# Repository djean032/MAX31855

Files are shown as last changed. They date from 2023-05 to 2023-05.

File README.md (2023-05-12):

# MAX31855

## Project Description
A solution to control and monitor four thermocouples using the MAX31855 Thermocouple Amplifier.

## Contents
- Arduino Sketch
- Custom MAX31855 Library
- KICAD Generated Schematic and PCB
- Test Data

## Arduino Sketch

The Arduino sketch is designed to print both to a serial monitor on a PC and a LCD screen that is mounted on the device.

## MAX31855 Library

Custom library that creates a class instance of each thermocouple amplifier and provides functions to read data, check errors, and do a rational polynomial caluclation to accurately determine the temperature. Additionally a weighted average is used to filter the signal, resulting in a significantly smoothed reading.

The initial form of this library uses a switch statement to select the proper conversion function based on thermocouple type, of which only type 'T' and 'K' are currently supported. Additional types will be added in the future, so this library can be universally used across all thermocouple and MAX31855 types.

## Schematic


## Circuit Features

#### Overview

The circuit consists of four MAX31855 thermocouple amplifiers that are connected to an Arduino Micro. The Arduino Micro is connected to the the thermocouple amplifiers via SPI, utilizing the SCK, MISO, and CS lines. The Arduino also communicates the data to a PC via serial while also displaying it on an onboard LCD.

#### MAX31855 Idiosyncrasies

The MAX31855 transmits a cold-junction compensated thermocouple temperature, a cold-junction temperature (from a thermistor), and several fault checks over 32 bits. The first 14 bits are the cold-junction compensated thermocouple temperature, the next 12 bits are the cold-junction temperature, and the rest of the bits are either reserved bits or denote various fault checks.

The MAX31855 uses a linear conversion to convert the thermocouple voltage to a temperature. Specifically the type 'T' version uses a factor of $52.18 \frac{\mu V}{\textdegree C}$, which shows significant deviations at room temperature from tabulated values. For this application, this is not a suitable conversion method, so a rational polynomial function was employed in software to more accurately  model the thermocouple response. The basic steps are to convert the measured thermocouple temperature to a voltage using the linear relationship stated in the datasheet. Then a switch statement is used to slect the type of chip to determine the appropriate coefficients for the rational polynomial function. Finally, the thermocouple voltage and coefficients are used in the rational polynomial function to compute a corrected temperature. This was tested at several temperatures and provides an acceptable level of accuracy.

#### Data Transfer

The data is simultaneously displayed on an LCD screen and transmitted to a PC via USB, where it is read into our lab's LabView program used to control our spectrometer. The data is "filtered" using a weighted average that takes a weighted average of the previous value with the current value. This weight can be adjusted via software. 30% of the previous value seems to be a sweet spot between data smoothing and quick response time.

#### Power Supply

The device is powered via a 9V external AC to DC power supply. In our current application, we have an approximately 15m USB cable, which is triple the specification for USB 2.0. 

#### Miscellaneous

The MAX31855 requires 3.3V to operate, while the Arduino Micro operates at 5V, so two bi-directional level shifters were used for the data and power lines for the thermocouple amplifiers.

## PCB


## Evaluation

#### Summary
Overall, once the rational polynomial function and filtering was added, the performance was adequate for our lab's needs. It successfully reads temperatures from boiling water down to cryogenic temperatures used in our lab's spectrometer.

#### Data
|        Cooling Bath         | Measured Temperature ($\degree C$) | Theoretical Value ($\degree C$) |
|:---------------------------:|:----------------------------------:|:-------------------------------:|
|          Ice Water          |                -2.0                |                0                |
|      Dry Ice + Acetone      |               -79.4                |               -78               |
|   Acetone + liquid N$^2$    |               -95.0                |               -94               |
| n-pentane +    liquid N$^2$ |              -133.5               |              -131               |
|        liquid N$^2$         |                -200                |              -196               |
|        Boiling Water        |               98.0                |         100                        |

Overall, the data matches very well with the theoretical values, within 2% error for all the cooling baths. The ice water and boiling water were done with tap water, so that is the likely source for the deviation there.

#### Future
Further improvements will be implemented in v2. These include capacitors to clean up the power supply and capacitors added on to the VCC and GND lines of the thermocouple amplifiers to prevent coupling of the data and power supply lines.

## v2 To-Do List
- Proper power supply design
	- Add appropriate capacitors to the input to reduce noise
- Add small capacitors to the VCC and GND lines of the thermocouple amplifiers to prevent coupling of the signal and the power lines.
- Transmit data over something other than USB

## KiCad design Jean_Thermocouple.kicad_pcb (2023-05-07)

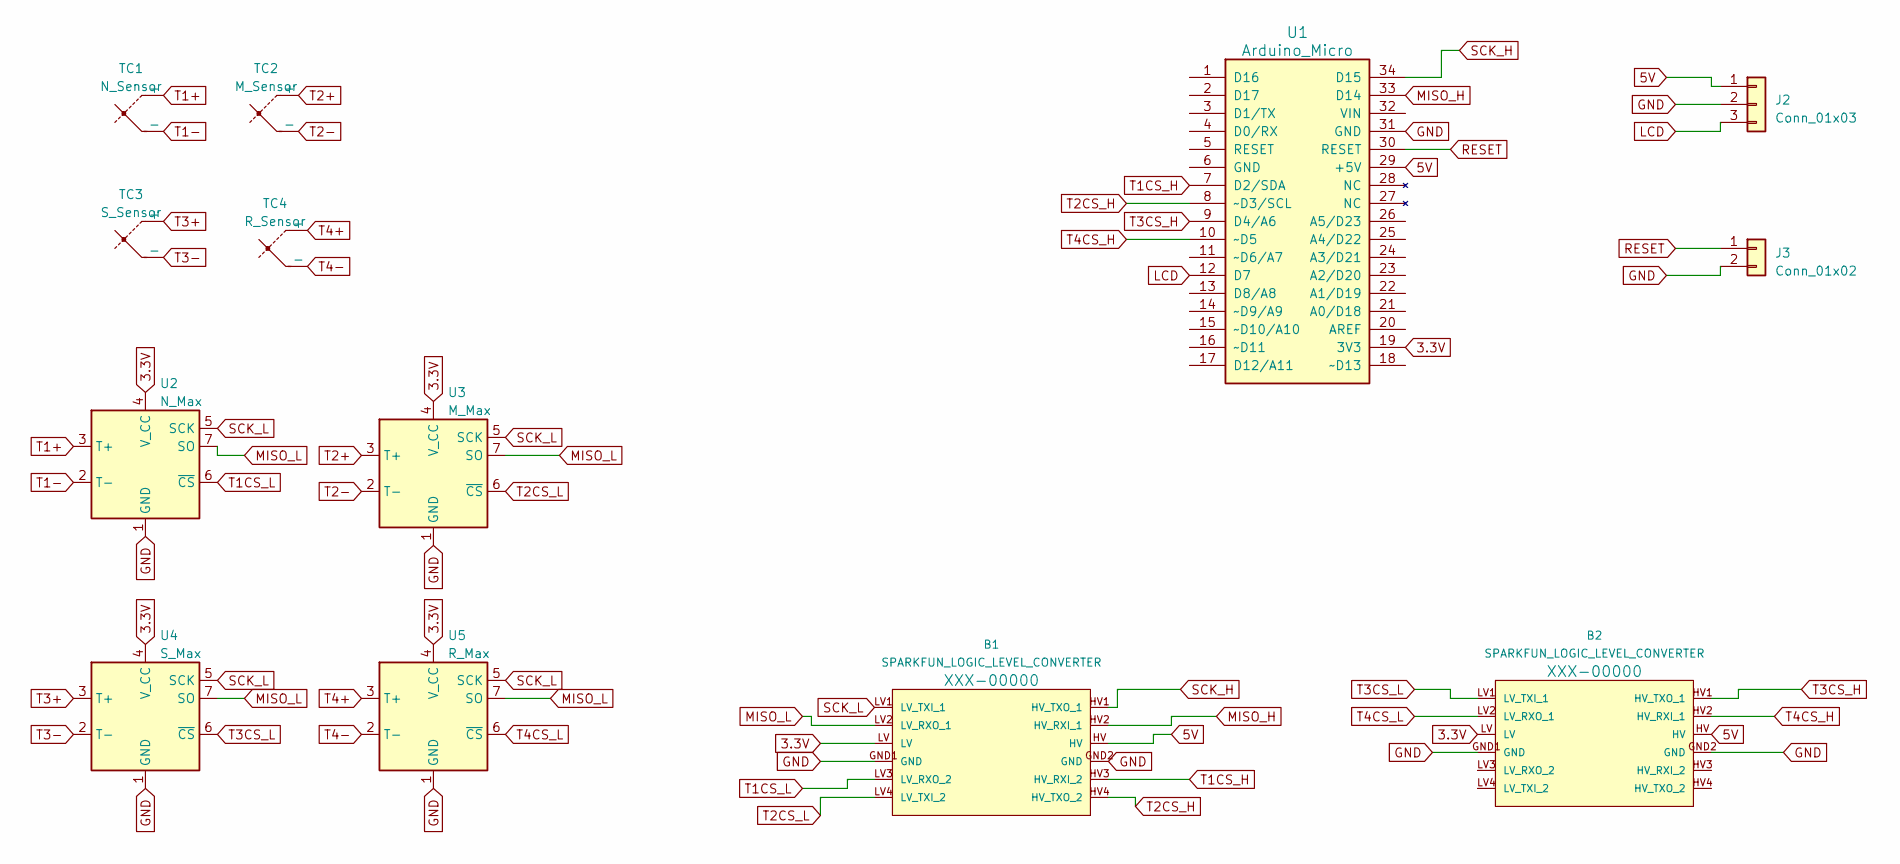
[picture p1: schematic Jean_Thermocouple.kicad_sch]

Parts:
B1, B2: SPARKFUN_LOGIC_LEVEL_CONVERTER
J2: Conn_01x03; PinHeader_1x03_P2.54mm_Vertical
J3: Conn_01x02; PinHeader_1x02_P2.54mm_Vertical
TC1: N_Sensor; PinHeader_1x02_P2.54mm_Vertical
TC2: M_Sensor; PinHeader_1x02_P2.54mm_Vertical
TC3: S_Sensor; PinHeader_1x02_P2.54mm_Vertical
TC4: R_Sensor; PinHeader_1x02_P2.54mm_Vertical
U1: Arduino_Micro
U2: N_Max; SOIC-8_3.9x4.9mm_P1.27mm
U3: M_Max; SOIC-8_3.9x4.9mm_P1.27mm
U4: S_Max; SOIC-8_3.9x4.9mm_P1.27mm
U5: R_Max; SOIC-8_3.9x4.9mm_P1.27mm

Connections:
3.3V: B1.LV, B2.LV, U1.19 (3V3), U2.4 (V_CC), U3.4 (V_CC), U4.4 (V_CC), U5.4 (V_CC)
5V: B1.HV, B2.HV, J2.1, U1.29 (+5V)
GND: B1.GND1 (GND), B1.GND2 (GND), B2.GND1 (GND), B2.GND2 (GND), J2.2, J3.2, U1.31 (GND), U2.1 (GND), U3.1 (GND), U4.1 (GND), U5.1 (GND)
LCD: J2.3, U1.12 (D7)
MISO_H: B1.HV2 (HV_RXI_1), U1.33 (D14)
MISO_L: B1.LV2 (LV_RXO_1), U2.7 (SO), U3.7 (SO), U4.7 (SO), U5.7 (SO)
RESET: J3.1, U1.30 (RESET)
SCK_H: B1.HV1 (HV_TXO_1), U1.34 (D15)
SCK_L: B1.LV1 (LV_TXI_1), U2.5 (SCK), U3.5 (SCK), U4.5 (SCK), U5.5 (SCK)
T1+: TC1.1 (+), U2.3 (T+)
T1-: TC1.2 (-), U2.2 (T-)
T1CS_H: B1.HV3 (HV_RXI_2), U1.7 (D2/SDA)
T1CS_L: B1.LV3 (LV_RXO_2), U2.6 (~CS)
T2+: TC2.1 (+), U3.3 (T+)
T2-: TC2.2 (-), U3.2 (T-)
T2CS_H: B1.HV4 (HV_TXO_2), U1.8 (~D3/SCL)
T2CS_L: B1.LV4 (LV_TXI_2), U3.6 (~CS)
T3+: TC3.1 (+), U4.3 (T+)
T3-: TC3.2 (-), U4.2 (T-)
T3CS_H: B2.HV1 (HV_TXO_1), U1.9 (D4/A6)
T3CS_L: B2.LV1 (LV_TXI_1), U4.6 (~CS)
T4+: TC4.1 (+), U5.3 (T+)
T4-: TC4.2 (-), U5.2 (T-)
T4CS_H: B2.HV2 (HV_RXI_1), U1.10 (~D5)
T4CS_L: B2.LV2 (LV_RXO_1), U5.6 (~CS)

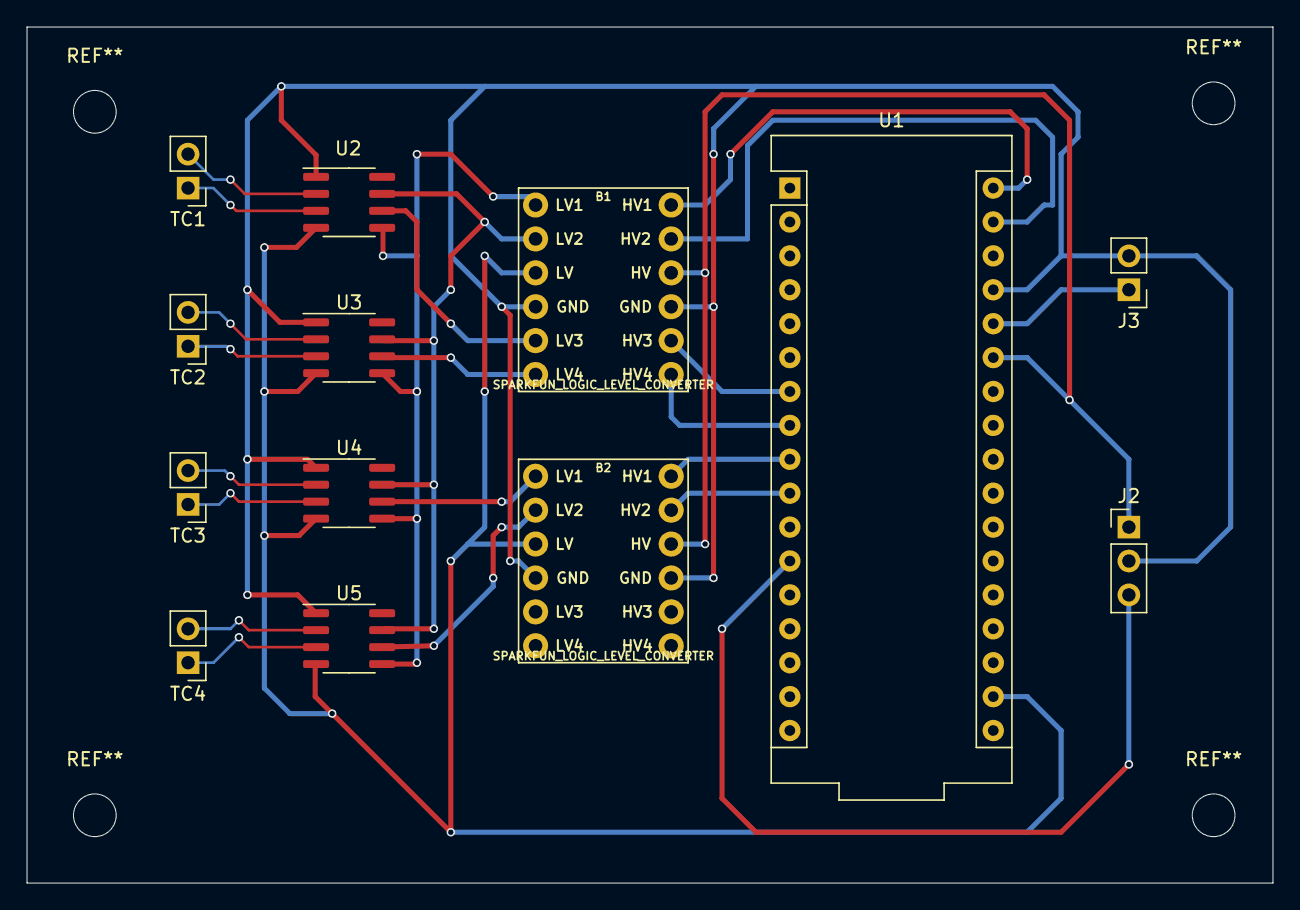
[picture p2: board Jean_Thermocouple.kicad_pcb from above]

Board: 2 copper layers, 93.3 x 64.1 mm, 13 parts (0 on the bottom side), 25 nets.

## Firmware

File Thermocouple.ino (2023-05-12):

/*
Thermocouple.ino - Sketch used to control 4 thermocouples with MAX31855 amplifiers.

Created by Dairen Jean 6MAY23.
*/


#include <SPI.h>
#include <SoftwareSerial.h>
#include "MAX31855.h"


/*
Define the pins for the MAX31855

For the data and clock pins, use the standard Arduino pins MISO (Master In Slave Out) and SCK (clock)

For the slave select or chip select pins, any of the digital pins work. In this example, 2-5 are chosen.

*/
#define MAXDO   MISO
#define MAXCS1  2
#define MAXCS2  3
#define MAXCS3  4
#define MAXCS4  5
#define MAXCLK  SCK
#define FILTER_WEIGHT 0.3

// Initialize the thermocouples using an array of pointers to their location, so we can iterate over them in our loop function.
MAX31855 *thermocouple[] = {new MAX31855(MAXCLK, MAXCS1, MAXDO, 'T'),new MAX31855(MAXCLK, MAXCS2, MAXDO, 'T'),new MAX31855(MAXCLK, MAXCS3, MAXDO, 'T'),new MAX31855(MAXCLK, MAXCS4, MAXDO, 'T')};

// Initialize our LCD screen which is connected to digital pin 7 on our Arduino.
SoftwareSerial LCD = SoftwareSerial(255,7);


void setup() {

  pinMode(7, OUTPUT);
  digitalWrite(7, HIGH);

  for (int i=0; i<4; i++)
  {
    (*thermocouple[i]).begin();
  }
  // Initializing our Serial communications
  Serial.begin(9600);
  LCD.begin(9600);

  // Turns display on, with no cursor and no blink
  LCD.write(22);

  // Turns backlight on.
  LCD.write(17);

  // Fault checking each of our thermocouples.
  for (int i=0; i<4; i++)
  {
    int32_t bits = (*thermocouple[i]).readBits();
    String fault = (*thermocouple[i]).readError(bits);
    Serial.println(fault);
    LCD.write(12);
    LCD.print(fault);
  }

  // Slight delay so the error messages can be read
  delay(5000);
  // Let's clear the screen in preparation
  LCD.write(12);
}

void loop() {

  // Instantiating our low pass filters, which are weighted moving averages that use a weight, alpha, to determine how much of the previous value to carry forward.
  LowPassFilter *filter[] = {new LowPassFilter(FILTER_WEIGHT),new LowPassFilter(FILTER_WEIGHT),new LowPassFilter(FILTER_WEIGHT),new LowPassFilter(FILTER_WEIGHT)};

  // Setup serial and LCD for print operationos
  Serial.println();
  LCD.write(12);

  // Time to loop through our pointer array for the thermocouples.
  for (int i=0; i<4; i++)
  {
    double temp = 0;
    double therm = 0;
    int32_t bits = 0;

    bits = (*thermocouple[i]).readBits();
    temp = (*thermocouple[i]).correctedTempCelsius(bits);
    therm = (*thermocouple[i]).readInternal(bits);
    double filteredTemp = (*filter[i]).filter(temp);
    String tempString = "Sensor " + String(i) + ": " + String(filteredTemp);
    Serial.print(filteredTemp);
    Serial.print("\t");
    LCD.print(tempString);
    LCD.write(13);
  }
  delay(500);
}

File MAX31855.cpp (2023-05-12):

/*
MAX31855.cpp - Library for use with the MAX31855 Thermocouple amplifer.

Created by Dairen Jean 6MAY23.

Initial Support for Type T and K Thermocouples added on 6MAY23.
*/

#include "Arduino.h"
#include "SPI.h"
#include "MAX31855.h"

/*
Instantiate the MAX31855 class
*/

MAX31855::MAX31855(int8_t sclk, int8_t cs, int8_t miso, char type)
{
  _sclk = sclk;
  _cs = cs;
  _miso = miso;
  _type = type;
}

void MAX31855::begin(void)
{

  pinMode(_cs, OUTPUT);
  digitalWrite(_cs, HIGH);
  SPI.begin();

  delay(200);
}


/*
Function to read internal thermistor used to calculate cold-junction temperature.
*/

double MAX31855::readInternal(int32_t bits1)
{
  double tempCelsius;

  bits1 = bits1 >> 4; //strip fault bits and reserved bit
  tempCelsius = (bits1 & 0x000007FF);

  if (bits1 & 0x00000800)
  {
    bits1 = ~bits1; // invert due to two's complement
    tempCelsius = bits1 & 0x000007FF; // only care about lower 11 bits
    tempCelsius += 1; // add one two's complement
    tempCelsius *= -1; // convert to negative and multiply by resolution
  }
  tempCelsius *= 0.0625;
  return tempCelsius;
}

/*
Function to read the temperature calculated by the MAX31855.

The chip assumes a linear relationship throughout its measurment range. If more accuracy is desired, use the corrected temp function.
*/

double MAX31855::readCelsius(int32_t bits2)
{
  double tempCelsius;

    bits2 = bits2 >> 18; // strip all but 14-bit thermocouple data

    tempCelsius = (bits2 & 0x00001FFF);

    if (bits2 & 0x00002000) // check sign bit to determine if negative number
    {
      bits2 = ~bits2; // invert because the data is two's complement
      tempCelsius = bits2 & 0x00001FFF;
      tempCelsius += 1; //  add one because two's complement
      tempCelsius *= -1; // convert back to negative and multiply by resolution to get value
    }
    tempCelsius *= 0.25; // multiply by resolution

  return tempCelsius;
}

/*
Function to calculate the cold-junction compensated temperature of the thermocouple.
This uses the measured thermocouple voltage and uses a rational polynomial calculation to convert the voltage to temperature.

For more info, see: http://www.mosaic-industries.com/embedded-systems/microcontroller-projects/temperature-measurement/thermocouple/calibration-table
*/

double MAX31855::correctedTempCelsius(int32_t bits)
{

    double correctedTemp = 0;
    double deltaV = 0;
    double deltaTcj = 0;
    double wrongTemp = readCelsius(bits);
    double internalTemp = readInternal(bits);
    double To, Vo, p1, p2, p3, p4, q1, q2, q3;
    double Tocj, Vocj, p1cj, p2cj, p3cj, p4cj, q1cj, q2cj;
    double thermocoupleVoltage = 0;
    double coldJunctionVoltage = 0;

    // Switch statement that depends on the type of thermocouple used. Coefficients are dependent on which thermocouple is used.
    switch (_type)
    {
    case 'T':
    thermocoupleVoltage = (wrongTemp) * 0.05218;
    Tocj = 2.5000000E+01;
    Vocj = 9.9198279E-01;
    p1cj = 4.0716564E-02;
    p2cj = 7.1170297E-04;
    p3cj = 6.8782631E-07;
    p4cj = 4.3295061E-11;
    q1cj = 1.6458102E-02;
    q2cj = 0.0000000E+00;


    deltaTcj = internalTemp - Tocj;
    //coldJunctionVoltage = Vocj + (deltaTcj * (p1cj + deltaTcj * (p2cj + deltaTcj * (p3cj + deltaTcj * p4cj)))) / (1 + deltaTcj * (q1cj + deltaV * q2cj));
    //thermocoupleVoltage += coldJunctionVoltage;
      if(thermocoupleVoltage <= -4.648){
          To = -1.9243000E+02;
          Vo = -5.4798963E+00;
          p1 = 5.9572141E+01;
          p2 = 1.9675733E+00;
          p3 = -7.8176011E+01;
          p4 = -1.0963280E+01;
          q1 = 2.7498092E-01;
          q2 = -1.3768944E+00;
          q3 = -4.5209805E-01;
      }

      else if(thermocoupleVoltage <= 0 && thermocoupleVoltage > -4.648){
          To = -6.0000000E+01;
          Vo = -2.1528350E+00;
          p1 = 3.0449332E+01;
          p2 = -1.2946560E+00;
          p3 = -3.0500735E+00;
          p4 = -1.9226856E-01;
          q1 = 6.9877863E-03;
          q2 = -1.0596207E-01;
          q3 = -1.0774995E-02;
      }

      else if(thermocoupleVoltage <= 9.288 && thermocoupleVoltage > 0){
          To = 1.3500000E+02;
          Vo = 5.9588600E+00;
          p1 = 2.0325591E+01;
          p2 = 3.3013079E+00;
          p3 = 1.2638462E-01;
          p4 = -8.2883695E-04;
          q1 = 1.7595577E-01;
          q2 = 7.9740521E-03;
          q3 = 0.0000000E+00;
      }
          else{
          To = 3.0000000E+02;
          Vo = 1.4861780E+01;
          p1 = 1.7214707E+01;
          p2 = -9.3862713E-01;
          p3 = -7.3509066E-02;
          p4 = 2.9576140E-04;
          q1 = -4.8095795E-02;
          q2 = -4.7352054E-03;
          q3 = 0.0000000E+00;
      }
    break;

    case 'K':
      thermocoupleVoltage = (wrongTemp - internalTemp) * 0.041276;


      Tocj = 2.5000000E+01;
      Vocj = 1.0003453E+00;
      p1cj = 4.0514854E-02;
      p2cj = -3.8789638E-05;
      p3cj = -2.8608478E-06;
      p4cj = -9.5367041E-10;
      q1cj = -1.3948675E-03;
      q2cj = -6.7976627E-05;


      deltaTcj = internalTemp - Tocj;
      //coldJunctionVoltage = Vocj + (deltaTcj * (p1cj + deltaTcj * (p2cj + deltaTcj * (p3cj + deltaTcj * p4cj)))) / (1 + deltaTcj * (q1cj + deltaV * q2cj));
      //thermocoupleVoltage += coldJunctionVoltage;
      if(thermocoupleVoltage <= -3.554){
          To = -1.2147164E+02;
          Vo = -4.1790858E+00;
          p1 = 3.6069513E+01;
          p2 = 3.0722076E+01;
          p3 = 7.7913860E+00;
          p4 = 5.2593991E-01;
          q1 = 9.3939547E-01;
          q2 = 2.7791285E-01;
          q3 = 2.5163349E-02;
      }

      else if(thermocoupleVoltage <= 4.096 && thermocoupleVoltage > -3.554){
          To = -8.7935962E+00;
          Vo = -3.4489914E-01;
          p1 = 2.5678719E+01;
          p2 = -4.9887904E-01;
          p3 = -4.4705222E-01;
          p4 = -4.4869203E-02;
          q1 = 2.3893439E-04;
          q2 = -2.0397750E-02;
          q3 = -1.8424107E-03;
      }

      else if(thermocoupleVoltage <= 16.397 && thermocoupleVoltage > 4.096){
          To = 3.1018976E+02;
          Vo = 1.2631386E+01;
          p1 = 2.4061949E+01;
          p2 = 4.0158622E+00;
          p3 = 2.6853917E-01;
          p4 = -9.7188544E-03;
          q1 = 1.6995872E-01;
          q2 = 1.1413069E-02;
          q3 = -3.9275155E-04;
      }
      else if(thermocoupleVoltage <= 33.275 && thermocoupleVoltage > 16.397){
          To = 6.0572562E+02;
          Vo = 2.5148718E+01;
          p1 = 2.3539401E+01;
          p2 = 4.6547228E-02;
          p3 = 1.3444400E-02;
          p4 = 5.9236853E-04;
          q1 = 8.3445513E-04;
          q2 = 4.6121445E-04;
          q3 = 2.5488122E-05;
      }
          else{
          To = 1.0184705E+03;
          Vo = 4.1993851E+01;
          p1 = 2.5783239E+01;
          p2 = -1.8363403E+00;
          p3 = 5.6176662E-02;
          p4 = 1.8532400E-04;
          q1 = -7.4803355E-02;
          q2 = 2.3841860E-03;
          q3 = 0.0000000E+00;
      }
      break;
    }
  deltaV = thermocoupleVoltage - Vo;
  correctedTemp = To + (deltaV * (p1 + deltaV * (p2 + deltaV * (p3 + deltaV * p4)))) / (1 + deltaV * (q1 + deltaV * (q2 + deltaV * q3)));
  return correctedTemp;
}

/*
Function to read errors from the thermocouples.
*/

String MAX31855::readError(int32_t bits3)
{
  String fault;
  if (bits3 & 0x00010000) // check if fault bit set
  {
    // switch statement that checks last three bits values to determine fault.
    switch (bits3 & 0x00000007)
    {
      case 0x01:
        fault = "No Thermocouple Connected";
        break;

      case 0x02:
        fault = "Thermocouple Shorted to GND";
        break;

      case 0x03:
        fault = "Thermocouple Shorted to VCC";
        break;

      default:
      fault = "No faults detected.";
      break;
    }
  }
  return fault;
}

/*
Function to read in the 32-bit output from the MAX31855.

It uses bitbanging to go through the bits, so they can be preserved for other operations.
*/

int32_t MAX31855::readBits()
{
  int32_t dataBuffer = 0;

  digitalWrite(_cs, LOW);                                          //stop  measurement/conversion
  delayMicroseconds(1);                                            //pulse fall time > 100nS
  digitalWrite(_cs, HIGH);                                         //start measurement/conversion

  delay(100);

  digitalWrite(_cs, LOW);                                          //set software CS low to enable SPI interface for MAX31855

  SPI.beginTransaction(SPISettings(5000000, MSBFIRST, SPI_MODE0));  // Start transaction at 14MHz MSB
  dataBuffer = SPI.transfer(0);                     // Read a byte
  dataBuffer <<= 8;                                 // Shift over left 8 bits
  dataBuffer |= SPI.transfer(0);                    // Read a byte
  dataBuffer <<= 8;                                 // Shift over left 8 bits
  dataBuffer |= SPI.transfer(0);                    // Read a byte
  dataBuffer <<= 8;                                 // Shift over left 8 bits
  dataBuffer |= SPI.transfer(0);                    // Read a byte
  SPI.endTransaction();

  digitalWrite(_cs, HIGH);                                         //disables SPI interface for MAX31855, but it will initiate measurement/conversion

  SPI.endTransaction();                                            //de-asserting hardware CS & free hw SPI for other slaves
// uncomment this for raw data troubleshooting
  //Serial.print(dataBuffer, HEX);

  return dataBuffer;
}


// Instantiate Low Pass Filter
LowPassFilter::LowPassFilter(double alpha)
  : yPrev(0.0f)
{
  _alpha = alpha;
}


/*
Function to filter thermocouple data using a weighted moving average.
*/
double LowPassFilter::filter(double x)
{
  double y = (1.0 -_alpha) * yPrev + _alpha * x;
  yPrev = y;
  return y;
}
